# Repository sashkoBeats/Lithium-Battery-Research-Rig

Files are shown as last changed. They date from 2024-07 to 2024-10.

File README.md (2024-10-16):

# Lithium Battery Research Rig
University project development of a rig for 18650 lithium battery testing and research.   
End goal is an EV simulation rig for researching EV battery health and performance.   
Created by Aleksandar Zdravkov and Indra Erkens   
Fontys University of Applied Sciences   
S7 Project and CSA1/2 2022-2024   
   
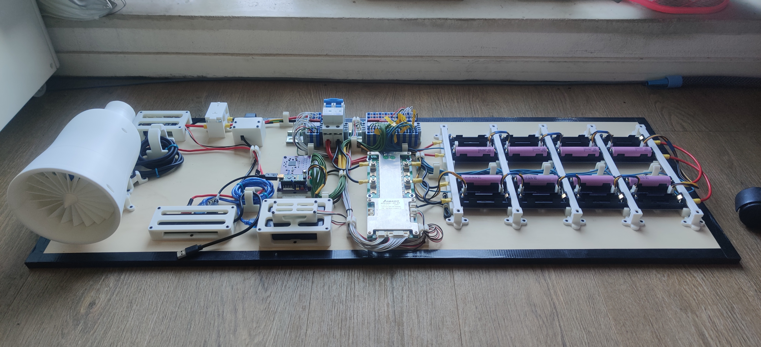
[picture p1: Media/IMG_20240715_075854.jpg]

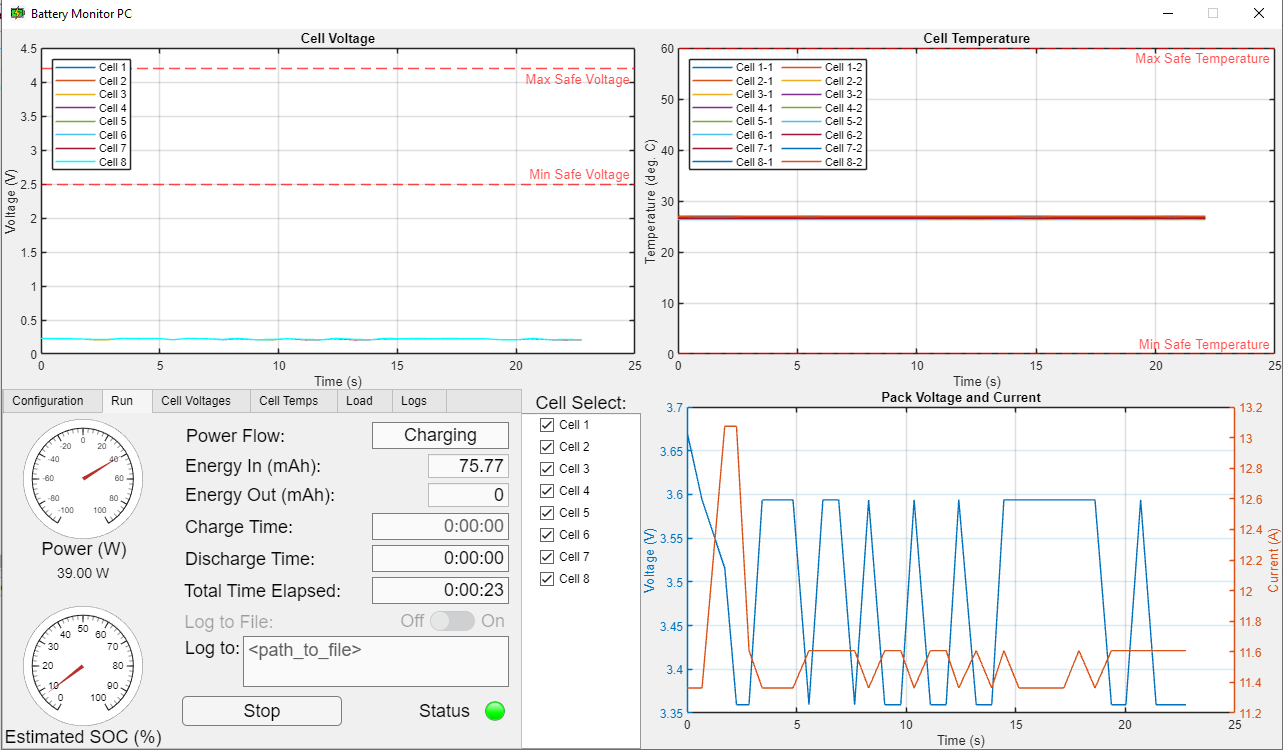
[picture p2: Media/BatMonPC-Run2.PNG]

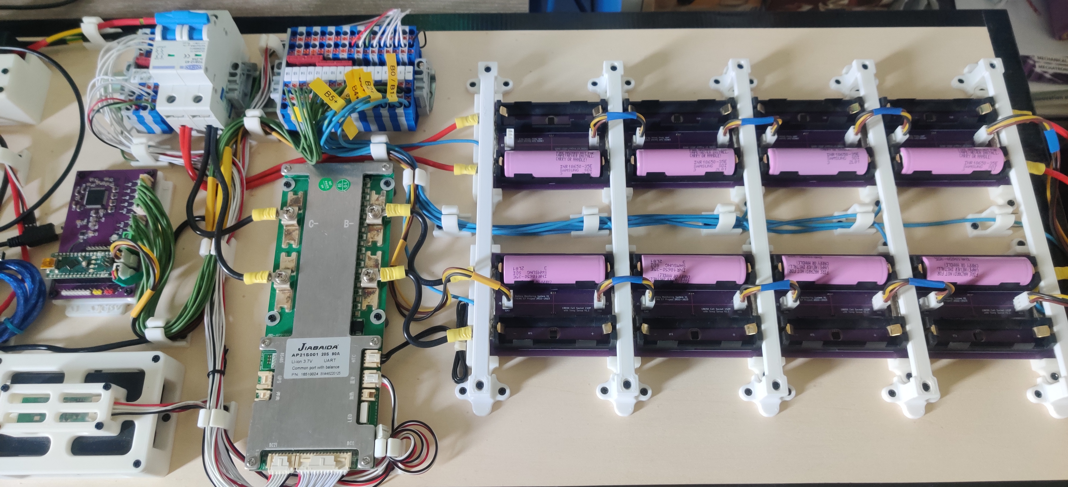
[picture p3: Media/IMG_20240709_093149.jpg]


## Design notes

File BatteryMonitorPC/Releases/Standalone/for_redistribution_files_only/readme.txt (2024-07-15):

BatteryMonitorPC Executable

1. Prerequisites for Deployment 

Verify that MATLAB Runtime(R2022b) is installed.
If not, you can run the MATLAB Runtime installer.
To find its location, enter
  
    >>mcrinstaller
      
at the MATLAB prompt.
NOTE: You will need administrator rights to run the MATLAB Runtime installer. 

Alternatively, download and install the Windows version of the MATLAB Runtime for R2022b 
from the following link on the MathWorks website:

    https://www.mathworks.com/products/compiler/mcr/index.html
   
For more information about the MATLAB Runtime and the MATLAB Runtime installer, see 
"Distribute Applications" in the MATLAB Compiler documentation  
in the MathWorks Documentation Center.

2. Files to Deploy and Package

Files to Package for Standalone 
================================
-BatteryMonitorPC.exe
-MCRInstaller.exe 
    Note: if end users are unable to download the MATLAB Runtime using the
    instructions in the previous section, include it when building your 
    component by clicking the "Runtime included in package" link in the
    Deployment Tool.
-This readme file 

3. Definitions

For information on deployment terminology, go to
https://www.mathworks.com/help and select MATLAB Compiler >
Getting Started > About Application Deployment >
Deployment Product Terms in the MathWorks Documentation
Center.

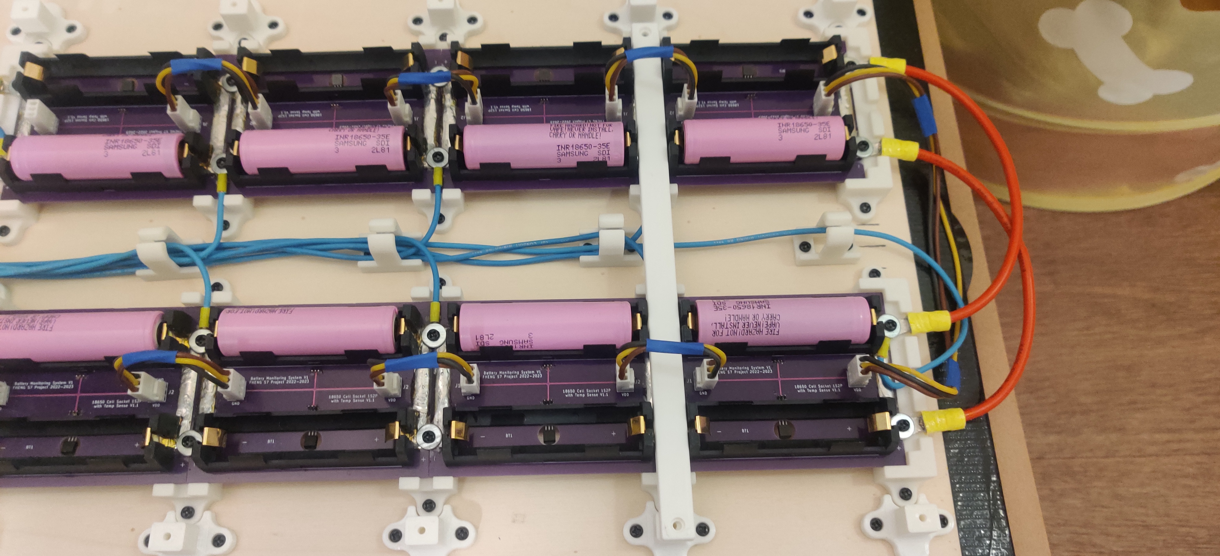
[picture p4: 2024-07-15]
Media/WIP/NiceToHaveFirstAttempt.jpg

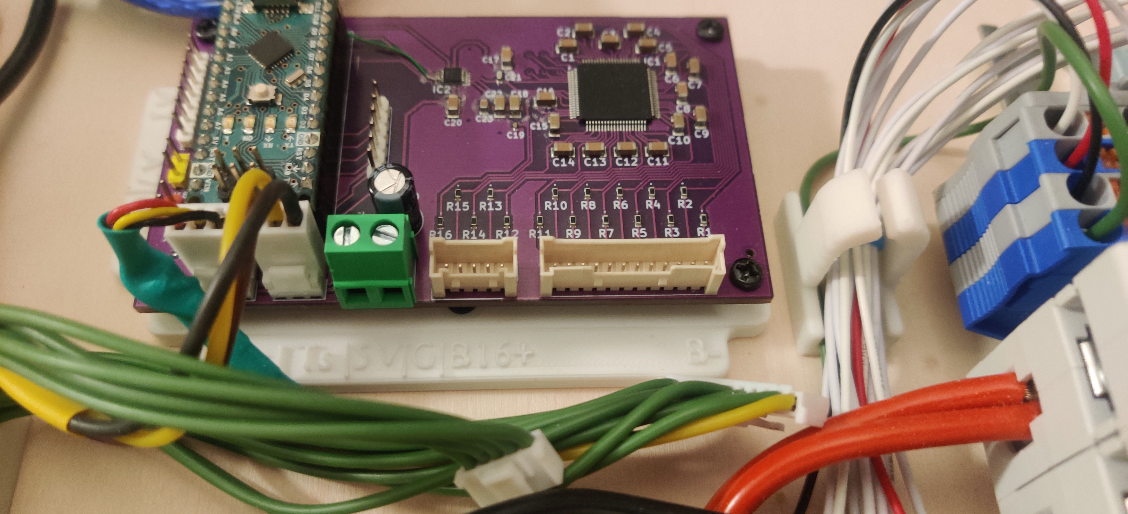
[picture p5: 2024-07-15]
Media/WIP/MonitorboardMount.jpg

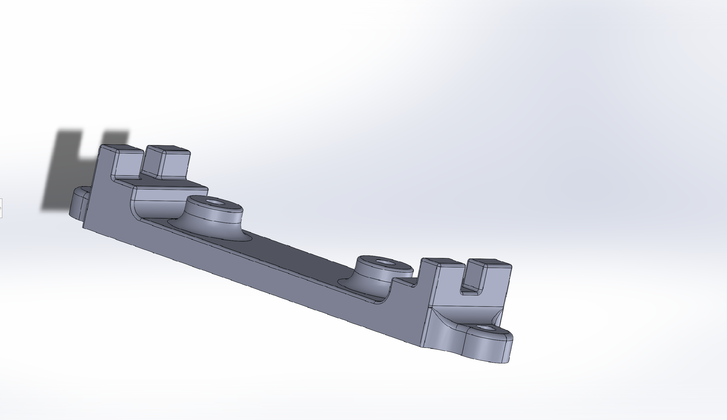
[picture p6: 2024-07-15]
Media/WIP/BatMountV2.png

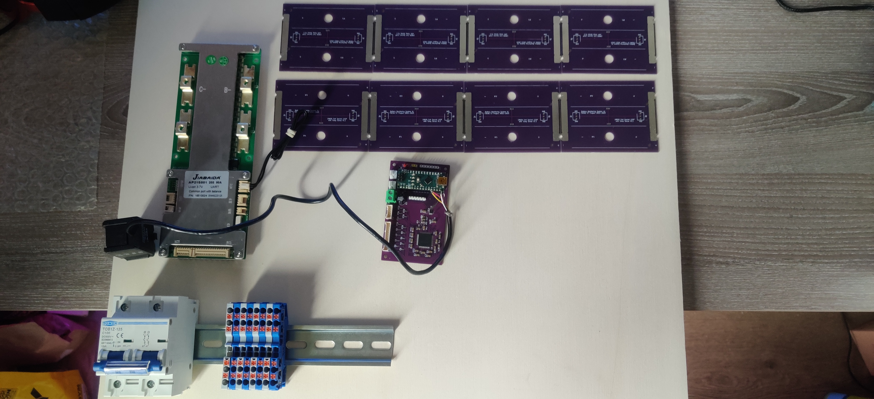
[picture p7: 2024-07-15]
Media/WIP/Layout.jpg

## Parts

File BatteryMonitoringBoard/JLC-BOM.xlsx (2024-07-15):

Comment | Designator | Footprint | JLCPCB Part #（optional）
100uF | C0 | CAPPRD250W50D680H1250 | C109392
1uF | C1, C2, C3, C4, C5, C6, C7, C8, C9, C10, C11, C12, C13, C14, C15, C16, C17, C18, C20, C22 | CAPC3216X180N | C13832
0.1uF | C19 | CAPC1005X55N | C1525
4.7nF | C21 | CAPC1608X90N | C85980
10uF | C23 | CAPC2012X140N | C1713
D_Schottky | D1, D2 | SOD2512X115N | C435857
MAX14921ECS+ | IC1 | QFP50P1400X1400X120-80N | C2932577
3k | R1, R2, R3, R4, R5, R6, R7, R8, R9, R10, R11, R12, R13, R14, R15, R16 | ERJ3EK__0603_ | C278616

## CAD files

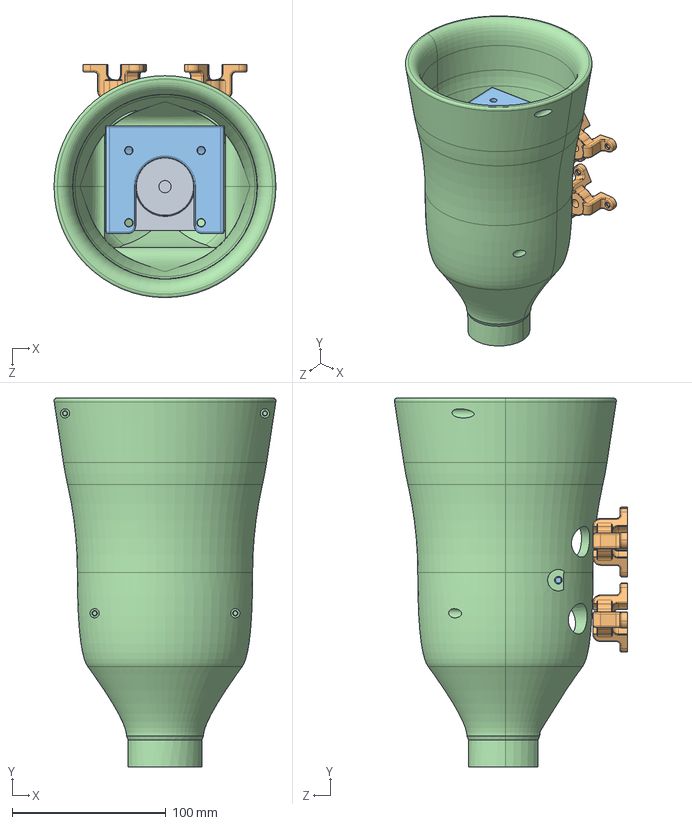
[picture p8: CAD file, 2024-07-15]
CAD/BLDC-Mount-Assy0/BLDC-Mount-Assy.SLDASM
144.3 x 240.0 x 151.7 mm
BatMt-BLDC x 4
BatMt-BLDC-TopV2
BLDC
FanDuct

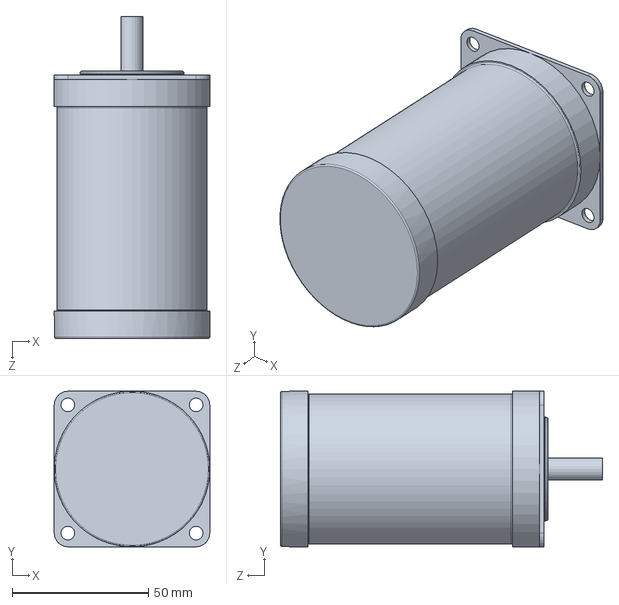
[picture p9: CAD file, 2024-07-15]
CAD/Assembly parts/BLDC.SLDPRT
57.0 x 57.0 x 118.0 mm

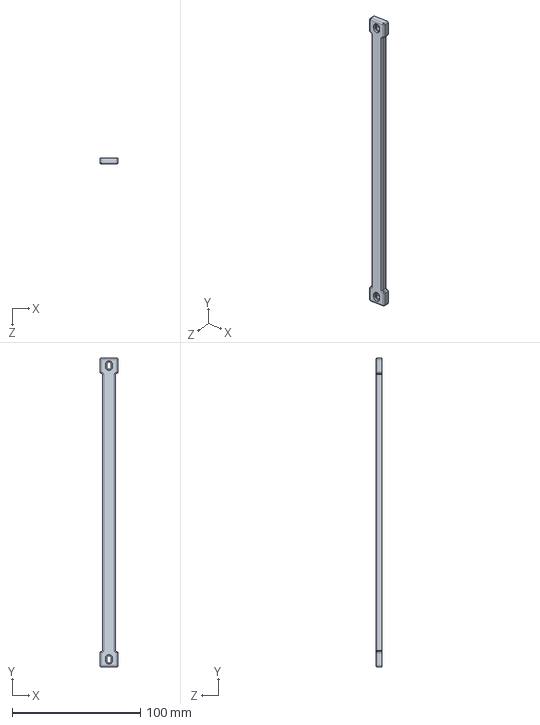
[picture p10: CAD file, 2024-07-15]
CAD/Battery Junction covers/BatMt-CoverV3-Top.SLDPRT
14.0 x 241.0 x 5.00 mm

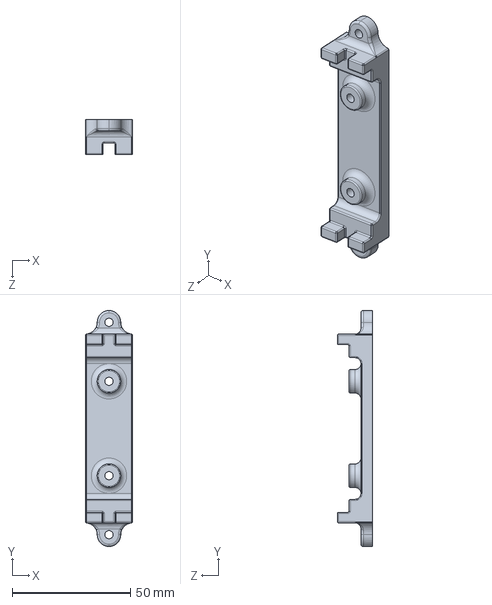
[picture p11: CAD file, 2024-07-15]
CAD/Battery PCB mounts/BatMt-Standoff-V2.SLDPRT
20.0 x 100.0 x 15.0 mm

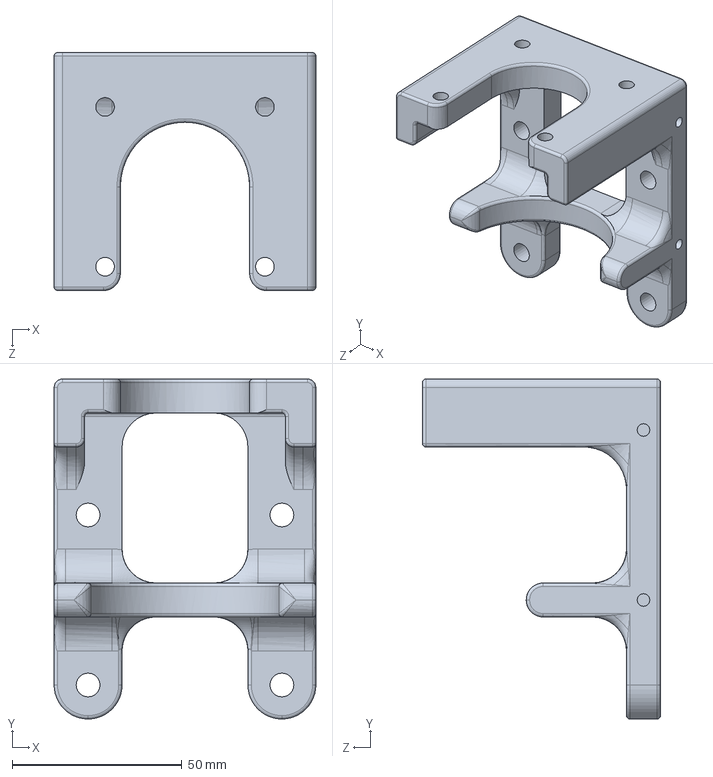
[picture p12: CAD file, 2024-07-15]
CAD/BLDC Bracket/BatMt-BLDC-TopV3.SLDPRT
77.0 x 100.0 x 70.0 mm

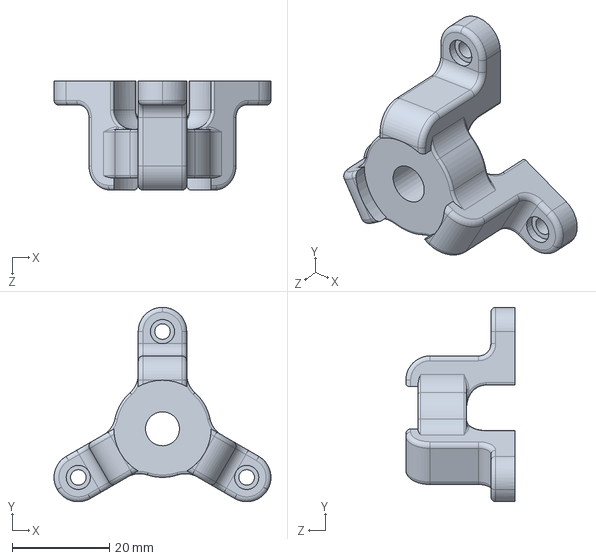
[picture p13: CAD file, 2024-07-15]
CAD/BLDC Mount/BatMt-BLDC.SLDPRT
44.6 x 40.0 x 22.5 mm

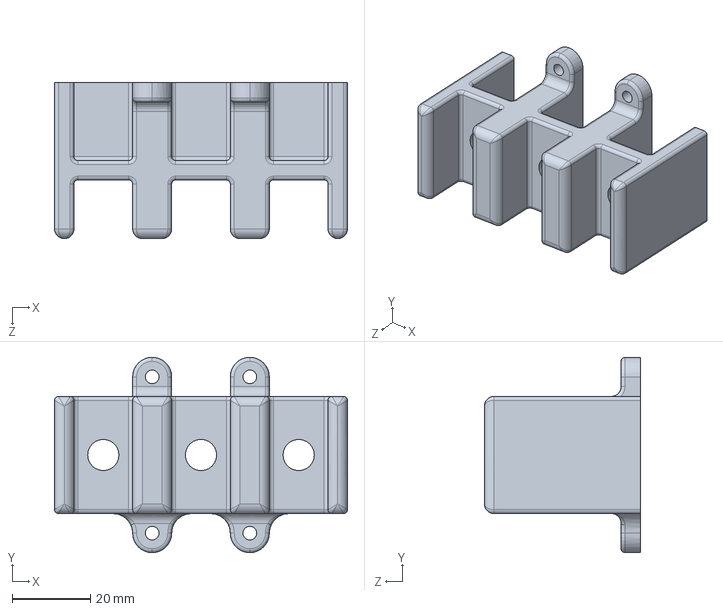
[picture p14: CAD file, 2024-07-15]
CAD/BLDC Power mount/BatMt-BLDC-Plugs.SLDPRT
75.0 x 50.0 x 40.0 mm

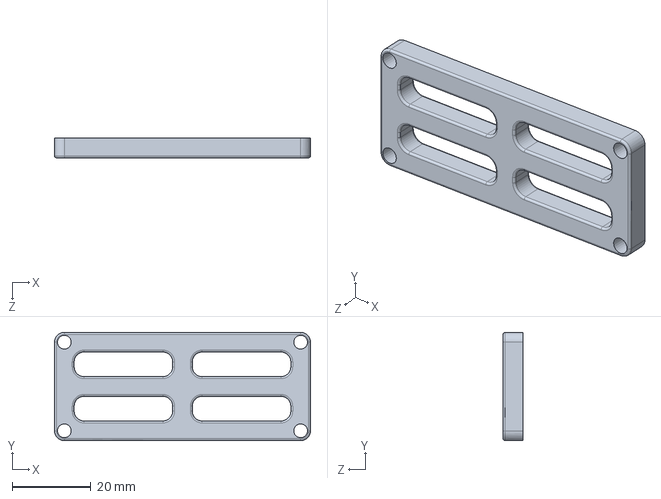
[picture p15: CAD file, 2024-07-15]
CAD/BMS UART box/BatUARTboxTopTop.SLDPRT
65.0 x 27.5 x 5.00 mm

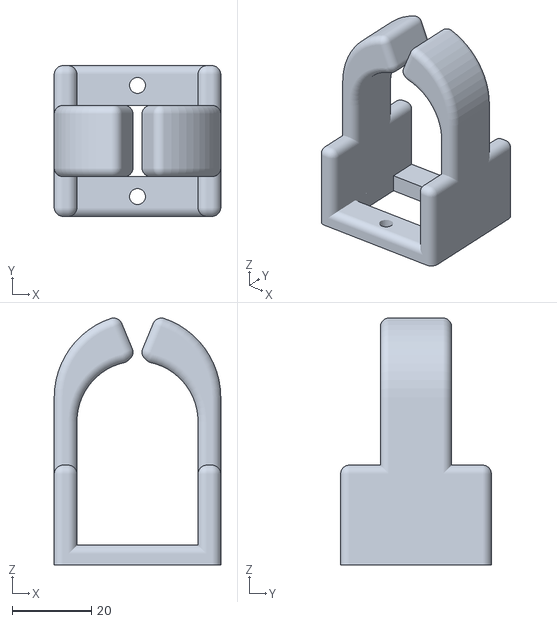
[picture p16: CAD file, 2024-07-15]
CAD/Cable clips/cableclip-large.stl
42.0 x 38.0 x 62.2

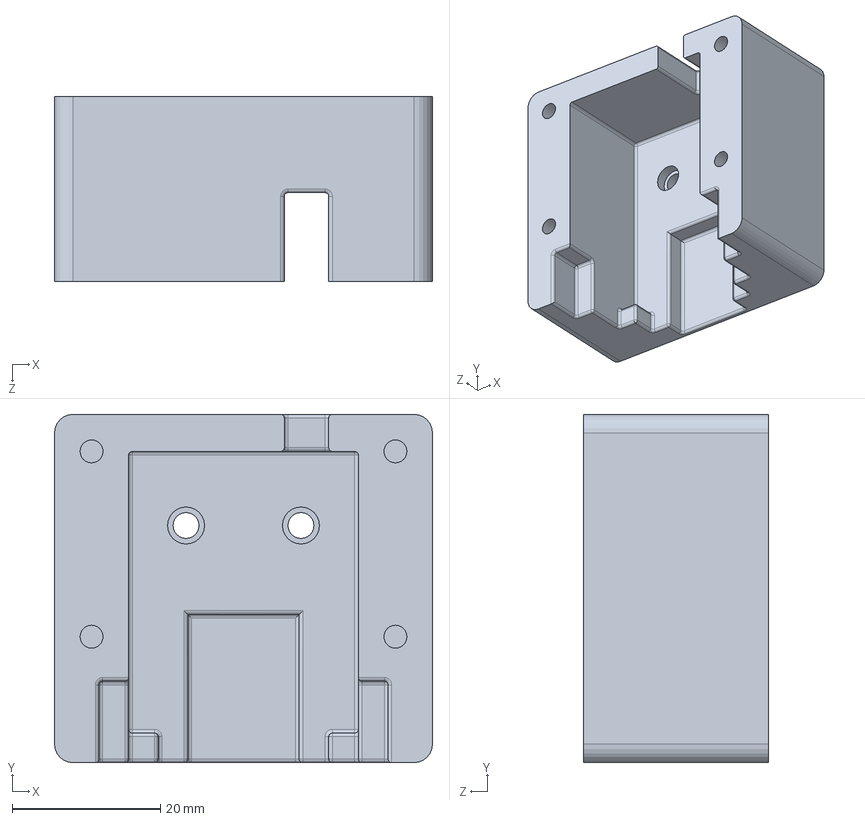
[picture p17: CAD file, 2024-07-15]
CAD/Current Sensor mount/BatMtCC.SLDPRT
51.0 x 47.0 x 25.0 mm

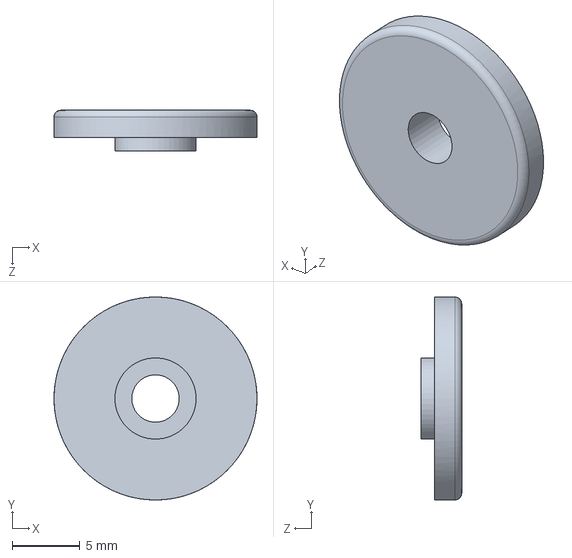
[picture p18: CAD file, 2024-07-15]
CAD/DIN-mount.SLDPRT
15.0 x 15.0 x 3.00 mm

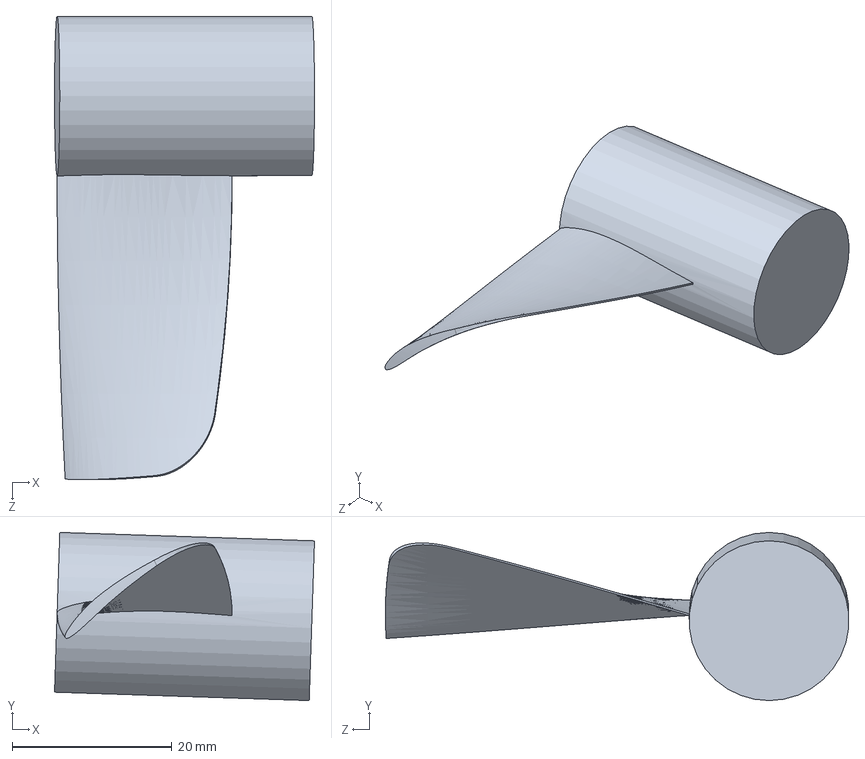
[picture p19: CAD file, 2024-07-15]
CAD/Fan/TurbofanAirfoil.SLDPRT
32.5 x 21.0 x 58.0 mm

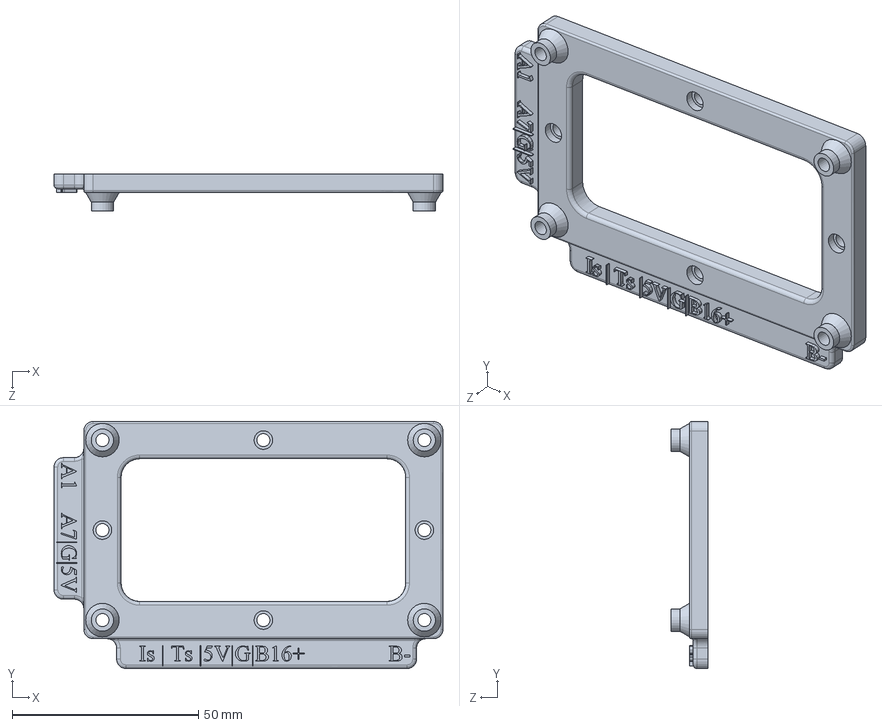
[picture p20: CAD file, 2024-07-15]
CAD/Monitor PCB mount/BatMtMonV2.SLDPRT
104.4 x 66.3 x 10.0 mm

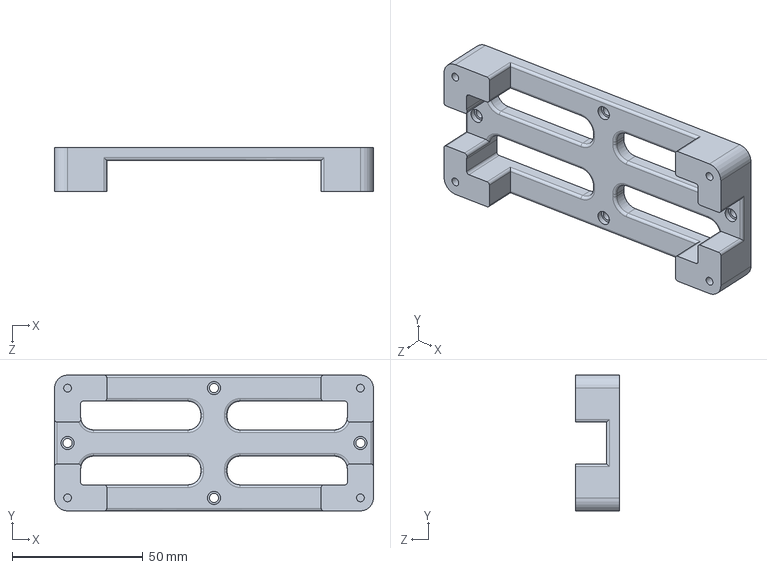
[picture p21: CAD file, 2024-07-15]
CAD/USB Hub box/BatUSBbox.SLDPRT
122.0 x 52.0 x 17.0 mm

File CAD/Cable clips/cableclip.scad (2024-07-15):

/*  cable management clip
    2017-10-13 Russell Salerno
    
    v2 with more automated parameter generation
    notes: open base is preferable as it makes the clamp more flexible & crack-resistant
    
*/


//Clip parameters

// [Distance clip extends from the wall]
depth = 65.5;

// [Height of arms]
height = 18.0;

// [Width of clip, cannot exceed depth]
width = 42.0;

// [Jaw thickness at top]
jaws = 9.0;

// [Space between jaws]
throat = 2.25;

// [Arm thickness]
side_thickness = 3.5;

// [Base thickness]
base_thickness = 5.0;

// [Distance each side wing extends from the arms]
base_sides = 10;

// [Leave at 0 for default ratio of 0.35*height]
base_height_ratio = 0;

// [Minkowski radius for edges]
radius = 2.25;

//Open or closed base? (choose closed if num_holes=1 or 3)
base_type = "open";  // [open, closed]

//Number of screw holes
num_holes = 2;      // [0, 1, 2, 3]

//Hole diameter
hole_diameter = 4;  // [0:10]

//Test render
test_render = true; // [true, false]

module null() {}

//sample sizes
//small
/*
depth = 28;
height = 10.0;
width = 15.0;
jaws = 4.0;
throat = 1.0;
side_thickness = 1.75;
base_thickness = 3.0;
base_sides = 8;
base_height_ratio = 0.25;        // [leave 0 for default]
radius = 0.75;
*/

//small/tall 
/* 
depth = 34;
height = 10.0;
width = 15.0;
jaws = 4.0;
throat = 1.0;
side_thickness = 2.0;
base_thickness = 3.0;
base_sides = 8;
base_height_ratio = 0;        // [leave 0 for default]
radius = 0.75;
*/

//medium
/*
depth = 38;
height = 12.0;
width = 25.0;
jaws = 5.0;
throat = 2.0;
side_thickness = 2.25;
base_thickness = 3.5;
base_sides = 9;
base_height_ratio = 0;        // [leave 0 for default]
radius = 0.95;
*/

//large (original size)
/*
depth = 65.5;
height = 18.0;
width = 42.0;
jaws = 9.0;
throat = 2.25;
side_thickness = 3.5;
base_thickness = 5.0;
base_sides = 10;
base_height_ratio = 0;        // [leave 0 for default]
radius = 2.25;
*/

$fn=60;
minkr=test_render ? 0:radius;   //minkowski takes a while to render, set to zero for testing

clipy=depth-minkr*2;
//clipx=width-minkr*2;
clipx=(width > depth)? clipy:width-minkr*2;     // width can't exceed depth
clipz=height-minkr*2;
clipthk=side_thickness-minkr;
clipjaws=jaws-minkr;
clipbase=base_thickness-minkr;

//throata1=22;
//throata2=25;
throata1=12*(depth/width);
throata2=10*(depth/(width-2*clipthk));
throaty=9/11*jaws;
throatx=throat+2*minkr;

basez=base_sides;
basey=(base_height_ratio == 0)? depth*0.35:depth*base_height_ratio;
baseholed=hole_diameter;

module throat() {
    translate([clipx/2, clipy-clipx/2, 0]) polygon([
        [clipx/2*-sin(throata1), clipx/2*cos(throata1)],
        [clipx/2, clipy],
        [clipx/2*sin(throata1), clipx/2*cos(throata1)], 
        [throatx/2, -throaty+clipx/2],
        [(clipx-clipthk*2)/2*sin(throata2), clipx/2*cos(throata2)-clipjaws-clipthk],
        [(clipx-clipthk*2)/2*-sin(throata2), clipx/2*cos(throata2)-clipjaws-clipthk],
        [-throatx/2, -throaty+clipx/2]]);
}

module base() {
    translate([0, 0, -basez]) linear_extrude(clipz+2*basez) difference() {
        square([clipx, basey]);
        translate([clipthk, clipbase, 0]) square([clipx-clipthk*2, basey-clipbase]);
    }
}

module holes() {
    translate([-minkr, 0, -minkr]) {

        if (num_holes == 1 || num_holes == 3) {
            translate([clipx/2+minkr, base_thickness, height/2]) rotate([90,0,0]) cylinder(d=baseholed, h=base_thickness+minkr);        // hole 1 of 1 hole base
         }

        if (num_holes == 2 || num_holes == 3){
            translate([clipx/2+minkr, base_thickness, -basez/2]) rotate([90,0,0]) cylinder(d=baseholed, h=base_thickness+minkr);        // hole 1 of 2 hole base
            translate([clipx/2+minkr, base_thickness, height+basez/2]) rotate([90,0,0]) cylinder(d=baseholed, h=base_thickness+minkr);  // hole 2 of 2 hole base
        }

        if (base_type == "open") {
            translate([side_thickness+minkr, 0, 0]) linear_extrude(height) square([clipx-clipthk*2-minkr*2, base_thickness]);   // hole for open base
        }
        translate([0, -2*minkr, -basez]) linear_extrude(clipz+2*basez+2*minkr) square([clipx+2*minkr, 2*minkr]);            // flatten the bottom
    }
}

module mainshape() {
    linear_extrude(clipz) difference() {
        hull() {
            square([clipx, 1]);
            translate([clipx/2, clipy-clipx/2, 0]) circle(d=clipx);
        }
        hull() {
            translate([clipthk, clipbase, 0]) square([clipx-clipthk*2, 1]);
            translate([clipx/2, clipy-clipjaws-(clipx-clipthk)/2, 0]) circle(d=clipx-clipthk*2);
        }
        throat();
    }
    base();
}


rotate ([90, 0, 0]) difference() {
    minkowski() {
        mainshape();
        sphere(r=minkr);
    }
    holes();
}

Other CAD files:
CAD/BLDC-Mount-Assy/BLDC-Mount-Assy.SLDASM
CAD/VESC box/BatVESCbox.SLDPRT
CAD/VESC Power In/BatVESCPowerBlockTop.SLDPRT
CAD/Assembly parts/Rubber-mount.SLDPRT
CAD/BLDC Bracket/BatMt-BLDC-Top.SLDPRT
CAD/BLDC Bracket/BatMt-BLDC-TopV2.SLDPRT
CAD/BLDC Mount/BatMt-BLDC.STL
CAD/BLDC Power mount/BatMt-BLDC-Plugs.STL
CAD/BLDC-Mount-Assy/FanDuct.SLDPRT
CAD/BLDC-Mount-Assy/FanDuctBot.SLDPRT
CAD/BLDC-Mount-Assy/FanDuctBot.STL
CAD/BLDC-Mount-Assy/FanDuctTop.SLDPRT
CAD/BLDC-Mount-Assy/Rubber-mount.SLDPRT
CAD/BLDC-Mount-Assy/TurboFan.SLDPRT
CAD/BLDC-Mount-Assy0/FanDuct.SLDPRT
CAD/BLDC-Mount-Assy0/Rubber-mount.SLDPRT
CAD/BLDC-Mount-Assy0/TurboFan.SLDPRT
CAD/BMS UART box/BatUARTbox.SLDPRT
CAD/BMS UART box/BatUARTbox.STL
CAD/BMS UART box/BatUARTboxTop.SLDPRT
CAD/BMS UART box/BatUARTboxTop.STL
CAD/BMS UART box/BatUARTboxTopTop.STL
CAD/BatMt-General-standoff-V2.SLDPRT
CAD/BatMt-General-standoff-V2.STL
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

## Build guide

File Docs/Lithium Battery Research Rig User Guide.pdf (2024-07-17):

# Lithium Battery Research Rig

# User Guide

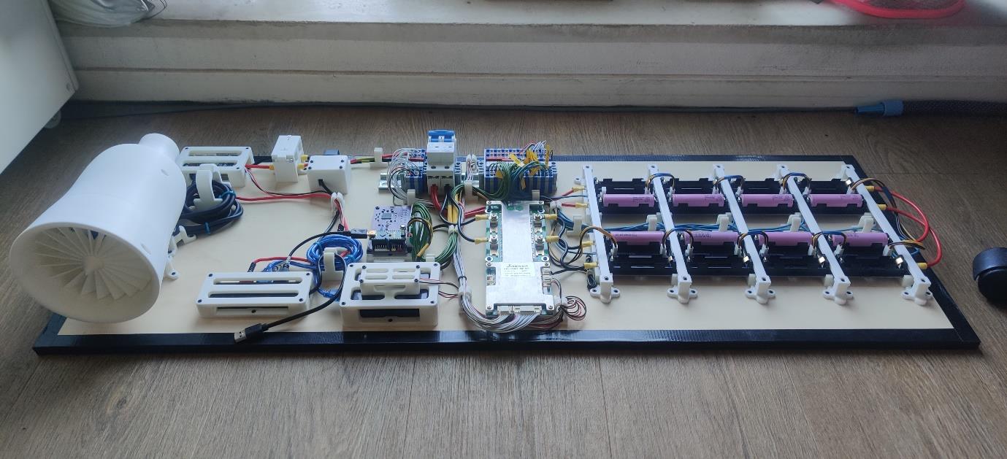
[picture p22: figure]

## Aleksandar Zdravkov Eindhoven

16/07/2024

## Table of Contents

Definitions | 3
SAFETY INFORMATION | 4
IMPORTANT INFORMATION | 5
Introduction | 5
Preparation for use | 7
Battery Monitor PC Application | 10
Preparation for storage | 12
Storage | 13
BMS | 13
Temperature sensors | 18
Load | 19
Resources | 19

Figure 1: Battery cell section of rig. Line of red dashes shows where to cut cables and break
board in case of terminal battery fault | 4
Figure 2: Battery Research Rig Setup | 5
Figure 3: Cold and dark battery rig | 7
Figure 4: First cell insert | 8
Figure 5: All cell holders populated for 8s1p configuration | 8
Figure 6: JDB BMS Homescreen after power up. All 8 cells detected | 9
Figure 7: Battery Monitor PC Configuration tab | 10
Figure 8: Battery Monitor Run tab | 11
Figure 9: Battery Monitor Run tab while running | 12
Figure 10: JBD Smart BMS mobile app dashboard | 14
Figure 11: JBD Mobile app navigation pane | 15
Figure 12: JBD Mobile app parameter settings page | 16
Figure 13: JBD Mobile app function setting page | 17
Figure 14: 18650 Lithium cell holder PCB with built-in DS18B20 digital temperature sensors... 18 Figure 15: Arduino program for detecing the unique device IDs of DS18B20 temperature
sensors | 19

# Definitions

AC | Alternating Current
ADC | Analog to Digital Converter
BMS | Battery Management System
BLDC | Brushless DC (Motor)
CAD | Computer Aided Design
CSA | Curriculum Supporting Activity
DC | Direct Current
DIY | Do-It-Yourself
EV | Electric Vehicle
ESC | Electronic Speed Controller
FET | Field Effect Transistor
GND | Ground
LFP | Lithium Iron Phosphate (LiFePO4)
R&D | Research and Development
RPM | Revolutions Per Minute
SOC | State of Charge
UART | Universal Asynchronous Receiver-Transmitter
USB | Universal Serial Bus

# SAFETY INFORMATION

This battery test and research rig is intended for use with 18650 size Lithium-based batteries. Most common of these are Li-Ion and Li-Poly, commonly found in smart devices (phones/laptops/tablets/etc.) and EV battery packs. These chemistries are incredibly dangerous as mishandling of the battery or subjecting it to abnormal operating conditions could cause it to enter a thermal runaway state. This is a terminal fault as Li-Ion and Li-Poly cells produce pure oxygen as a byproduct of the lithium in the cell reacting with the air and the other compounds in the cell structure as it’s disintegrating on fire. Therefore, a Li-Ion/Poly cell fire CANNOT be extinguished as the fire is essentially producing its own fuel. This generally does not apply to LiFePO4 batteries as their chemical composition makes them much more stable. When in thermal runaway state, LFP cells do not produce their own oxygen fuel. Instead, a failing LFP cell simply vents its electrolyte compound (PO4) as a gas/vapor through a one-way relief valve. The temperature reached during thermal runaway of LFP cells is also typically not high enough to cause an uncontrolled fire.
For the safety of the students and Fontys Engineering, it is important that students given access to this rig are well informed about the operational principles and hazards of lithium-based batteries. When the rig is in use, it MUST ALWAYS be accompanied by a container full of sand and/or dirt that can be used to dump a failing cell into to burn up in safety (as mentioned above, once a cell is in thermal runaway, it cannot be saved). If a cell fails (starts smoking/swelling/burning) while installed on the rig, pour the sand/dirt on top of it to try to limit the spread to the other cells in the rig. If the failing cell was successfully contained, wait for it to cool off and carefully remove it from the rig. The cell-holder PCB can be easily replaced if it suffers damage. In case covering a failing cell with sand/dirt does not contain the fire, you can attempt to save the rest of the setup by cutting all the wires between the batteries section of the rig and the electronics. This will allow you to break-off the batteries section of the plywood board and let it burn, saving the expensive monitoring electronics, BMS, loads, etc. ONLY DO THIS IF YOU ARE CONFIDENT YOU HAVE ENOUGH TIME UNTIL FIRE IS COMPLETELY OUT OF CONTROL TO EXECUTE THE PROCEDURE. IF UNSURE, JUST RUN AWAY AND CALL FOR HELP.

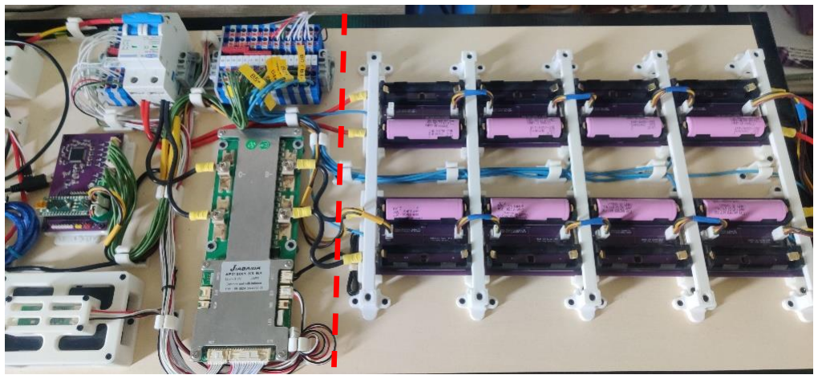
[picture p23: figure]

Figure 1: Battery cell section of rig. Line of red dashes shows where to cut cables and break board in case of terminal battery fault.

# IMPORTANT INFORMATION

Never leave battery cells in the rig unattended, especially while in storage! The BMS and Battery Monitoring board will draw power from any cells left in the holders and gradually drain them to 0V. Dropping below minimum spec sheet voltage is very bad for lithium cells so it should never be allowed to happen. Removing just the first or last cell in the stack does NOT prevent the drain from occurring in the other cells! ALL CELL HOLDERS MUST BE EMPTY WHEN THE RIG IS NOT IN USE!
It should go without saying that nothing “dumb” shall be done with any lithium cells at any point, especially when a cell is under load (DUT), that risks the safety of people and/or the research rig. Hitting, puncturing, burning/heating/freezing, overloading, shorting, or otherwise subjecting lithium cells to abnormal conditions can be deadly to you and your colleagues. Exercise great care and be on high alert when working with this rig and with lithium batteries in general!

# Introduction

This user guide goes over all the information related to the use of the lithium battery research rig. The rig was created over a span of 2 academic years, starting as a semester 7 project in the 2022-2023 academic year. The S7 project ended with only a general schematic of the intended final product and the PCB design of the battery monitoring board. As part of CSA 1 and 2 over the following 1.5 years, the project was worked on by 2 students in their free time in-between internships and work. The rig gradually took shape with additional functionality added to make it more feature complete. As of writing this guide, the rig is only missing a controllable mechanical load in order to be a fully functional EV simulation device. The rig is intended to be used by Fontys students to study health and performance of lithium batteries and by extension, EV battery packs. There are many topics of interest for research and development, but they will be discussed in a separate guide. The GitHub repository hosting this project includes all source code, CAD files, schematics, data sheets, etc. that were used in the execution of the project.

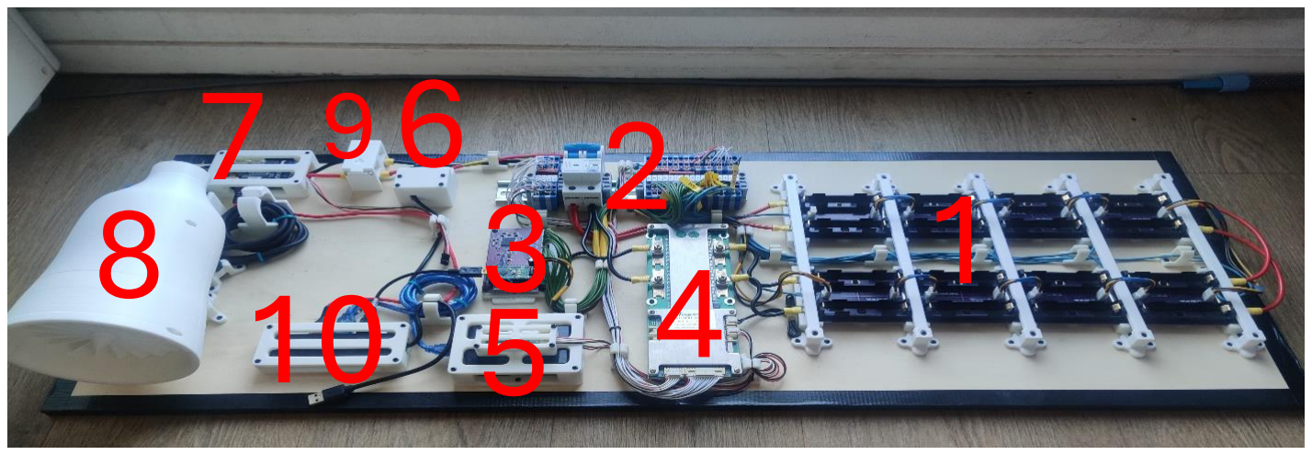
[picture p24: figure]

Figure 2: Battery Research Rig Setup.
Based on the figure above, a short description of each main component of the rig can be found below:

### 1. Battery cell stack

The rig is designed around an 8 series cells with 2 parallel for each (8s2p) configuration of 18650 Li-Ion/Poly/FePO4 batteries. This configuration and slight variations of it (+-1/2 cells in series or parallel) are commonly used for smaller personal EVs like E-bikes, E-scooters, E-skateboards, etc. The cells are laid out in quick-swappable cell holders on custom PCBs in 2 sections of 4 series PCBs. Pay attention to the direction of the sections – they are mirrored symmetrically, meaning the positive and negative side invert between the sections. Pay close attention to the polarity of the cells when installing them in the holders. Each battery holder PCB also has a digital temperature sensor installed underneath each cell. These are connected to the battery monitoring board via their dedicated 3-wire cables in daisy-chain configuration.

### 2. Distribution “box”

All cell taps (wires to each individual cell) are wired to a dedicated (for each cell) DIN-rail 4-port wire socket. The battery monitoring board and BMS connect to the box with the appropriate wiring scheme for correct operation of each device. Each wire socket has 1 port left uncopied, for future use (see R&D Guide). The box also includes a main DC-rated circuit breaker between the battery stack and any loads.

### 3. Battery Monitoring Board

Customed designed PCB housing a MAX14921 16-cell battery monitoring IC, a MAX11161/11163 16-bit ADC, and a socketed Arduino Nano MCU. The Arduino Nano interfaces with the 2 MAX chips via SPI to get battery and cell voltage data. It also fetches temperature data for each cell from the daisy chain and the current sensor data for total battery pack current. The data is transferred to PC in raw format via Serial for processing in real time with the help of a dedicated MATLAB Application.

### 4. JBD BMS

This is a commercial smart BMS that allows manual tuning of a wide variety of lithium battery protections. The BMS is required to keep the battery from unintentionally entering abnormal conditions. It’s configured for Li-Ion cells currently but needs to be reconfigured when different cell chemistries are used.

### 5. JBD Bluetooth and UART modules

These are the interfaces available for connecting with the JBD BMS. Only one of them can be used at a time since they share the same communication port on the BMS. By default, the BT module is connected, as it’s easier to configure the BMS with the smartphone app. Alternatively, the UART box can be connected instead and used in conjunction with an open-source application, BMS Tools JBD, which allows for monitoring and control of the BMS from a PC.

### 6. Current Transformer (sensor)

A split-core current transformer used to measure the total current going in or out of the battery pack. The sensor is bi-directional and rated for DC measurement. In the rig, the positive wire of the battery pack goes through the sensor. The sensor is rated for 5V power and signaling, providing an analog signal for measurements, which is read by the Arduino Nano.

### 7. Flipsky VESC 4.12

The electronic speed controller used to convert the battery pack’s DC power to 3-phase AC for driving the BLDC motor load. The VESC is extensively customizable, allowing for great load control when developing EV simulation runs.
8. 150W Electric Skateboard BLDC
A relatively big BLDC motor rated for up to 36V and up to 8A current draw to be used as an electrical load for the battery pack. The motor does not consume much power to reach its max RPM when no mechanical load is placed on it, which means it needs a controllable mechanical load to make the rig fully operational. Until such a solution is created or found, a turbine-type engine was built around the motor to keep it cool (it heats up when running for a while with no load).

### 9. Battery DC I/O Port

Underneath the plastic cover are 2 banana plug receptacles coming from the battery positive and negative wires. The port can be used for a variety of things, such as charging the whole battery stack, attaching external loads, or just probing for measurements. 10.USB Hub
Since the BMS, the battery monitoring board and the VESC all have USB interfaces for PC communication, a small USB hub is incorporated to simplify the connection to a PC for use with the rig.

# Preparation for use

This chapter covers the steps to take from “cold and dark” to configure the rig for use. When you begin work, the rig should look like the figure below, with no cells installed and DC circuit breaker in the OFF position.

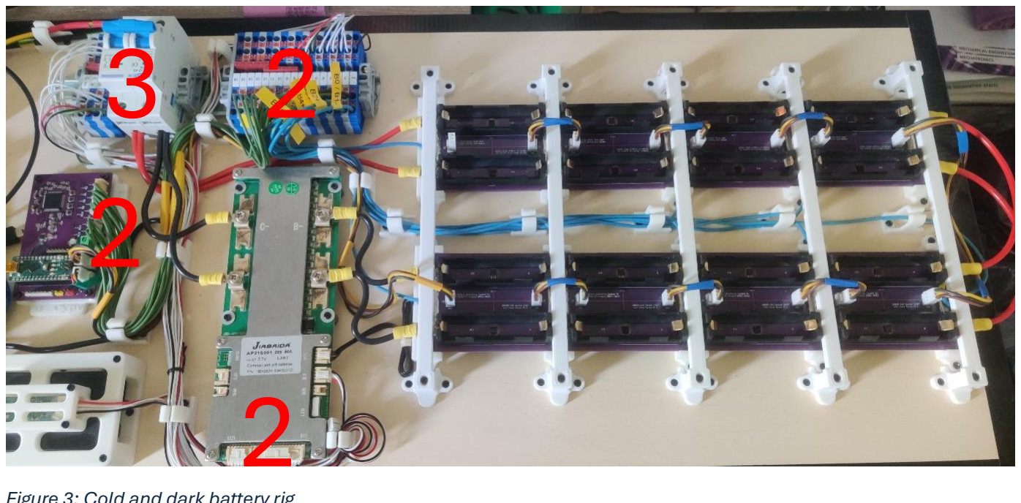
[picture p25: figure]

Figure 3: Cold and dark battery rig.
1. First, inspect the whole rig for any abnormalities, disconnected wires, etc. Once you make sure everything is looking proper, proceed with cable check.
2. Check all cables – All cell taps should be connected to their proper position in the cell stack and the distribution box. Check the BMS and battery monitoring board cables harnesses are connected.
3. With the DC breaker OFF, battery cells may now be inserted into the slots.
4. Insert cell into each holder, starting with cell 0 (closest to negative wires). If only 1 cell per segment in the series stack is used (so, 8s1p configuration), populate either only the BT1 or BT2 slots for each cell holder in the series. Pay attention to cell polarity!

4

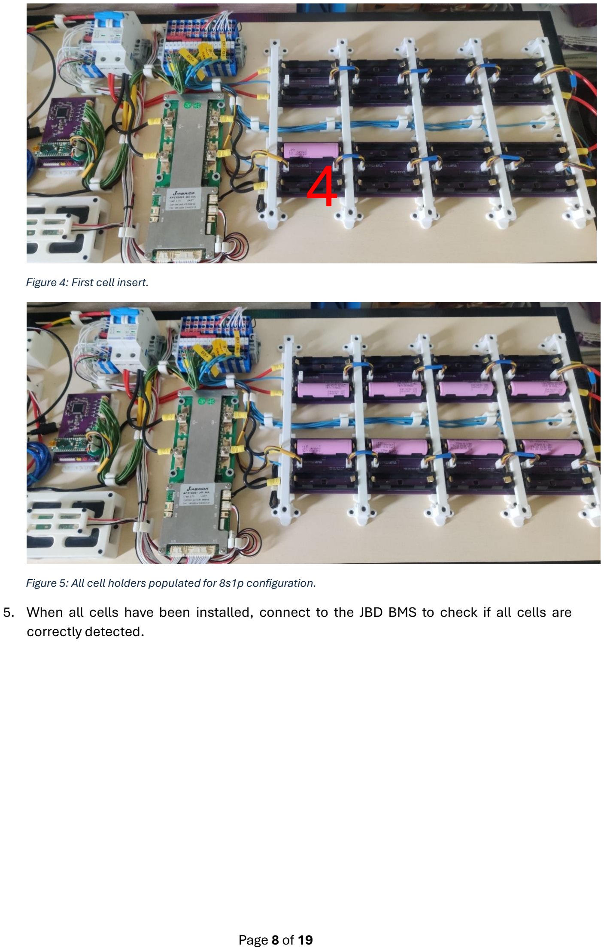
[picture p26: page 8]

Figure 4: First cell insert.

Figure 5: All cell holders populated for 8s1p configuration.
5. When all cells have been installed, connect to the JBD BMS to check if all cells are correctly detected.

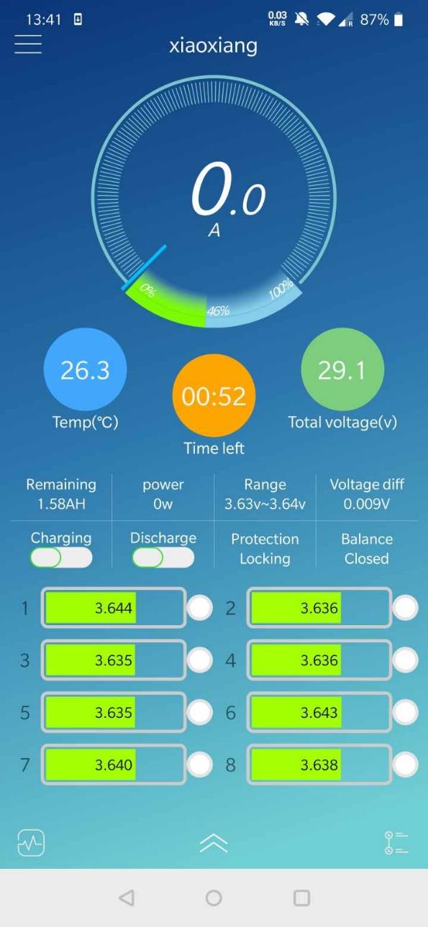
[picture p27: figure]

Figure 6: JDB BMS Homescreen after power up. All 8 cells detected.
6. Once the pack is correctly installed, the USB hub can be connected to a PC to power up the Arduino Nano on the battery monitoring board and provide an interface to the JBD UART box and the VESC.
7. The MATLAB Battery Monitor PC application can now be started and a connection with the Arduino Nano on the monitoring board can be established. The instructions for using the application can be found in the next chapter.
8. With the PC application configured and connected to the battery monitoring board, testing runs can executed.
9. Check that an adequate load is correctly attached to the DC circuit breaker. If all is good, flip the circuit breaker to the ON position. The VESC should light up and appear as a new COM port on the PC connected to the USB hub.
NOTE: If the load/VESC does not power up, check that the JBD BMS has switched on its Discharge FETs.
10. With the load configured and online, the battery rig is ready for science. Students shall prepare a test plan or protocol to conduct and commence its execution at this point.

# Battery Monitor PC Application

In order to process the incoming battery data from the monitoring board, a special MATLAB App was developed. The application polls the battery monitoring board at a user defined polling rate (0.5s default, 0.2s minimum) for all battery data that it collects (voltage, current, temperature) in raw format. The data is converted to usable values and displayed on 3 MATLAB graph windows. The application is packaged both as a MATLAB App module and as standalone application installer that includes a MATLAB runtime necessary to run. So MATLAB is technically not required to run the app. The main functions of the app are described below. Most fields and widgets in the application also show a helpful tooltip when hovered upon with the mouse pointer to guide the user.

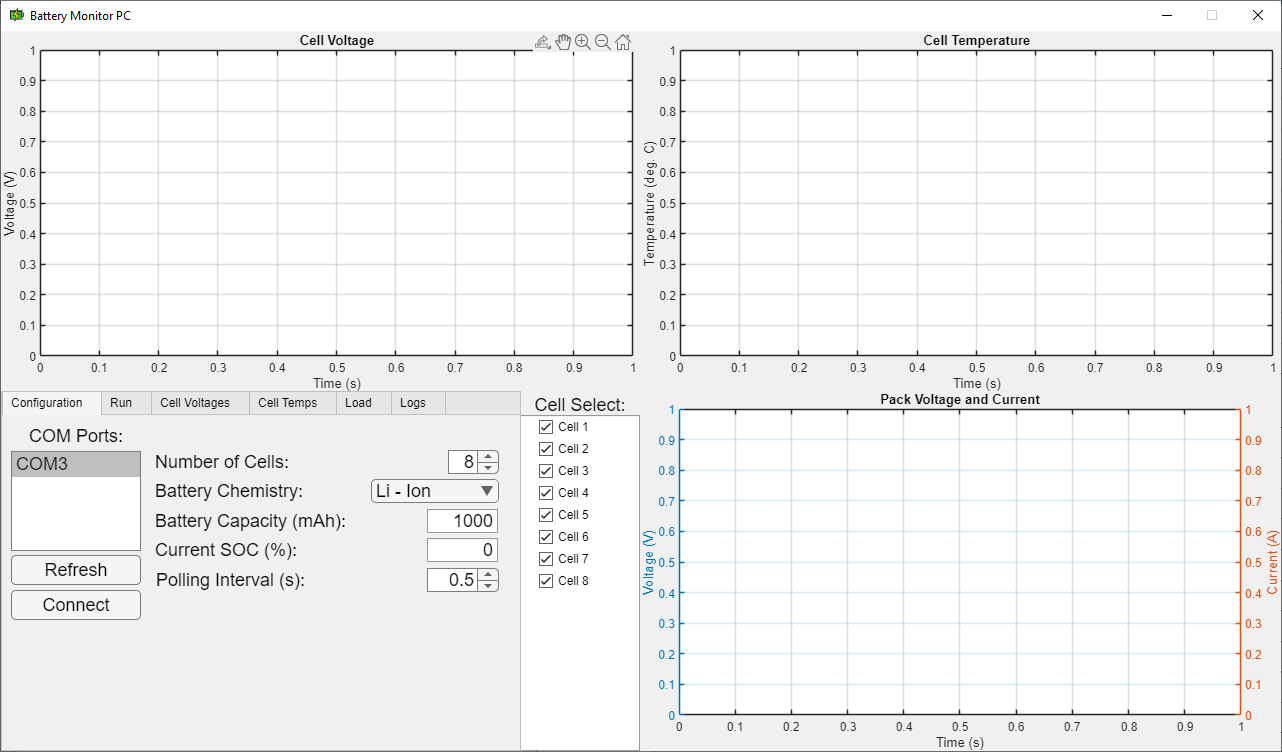
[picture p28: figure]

Figure 7: Battery Monitor PC Configuration tab.
The figure above shows the interface of the Battery Monitor PC application when it’s launched. The top left and the two right quadrants of the application window are permanently occupied by the voltage, temperature and voltage/current graphs. The bottom left quadrant is where all the control UI is located, separated into tabs that group related functionality and/or data displays together. If the battery monitoring board is plugged in, it will show up as a COM port in the list at the left of the Configuration page. To the right of it are the parameters for the cell stack currently installed in the rig. All values except current SOC and rated battery capacity MUST be configured before connecting to the Arduino on the monitoring board, as they are required for configuration of the Arduino and will become locked after hitting “Connect”. Once connected to the monitoring board Arduino, cyclic data polling will start at the specified polling rate, but the graphs will not work at this time. To go easy on the PC running the app, the graphs are only going to start updating once a test run is initiated via the Run tab. If it’s needed to check battery data before starting a run, the fields in the Cell Voltages and Cell Temps tabs will always update any time there is new data available. The Cell Select window scales automatically with the number of cells selected and only controls which cell data is displayed on the graphs. The data for all cells up to the selected number of cells is always retrieved from the Arduino and written to the file log, if enabled. Once configured and connected to the Arduino, the Run tab becomes the main window for the bottom left quadrant of the app.

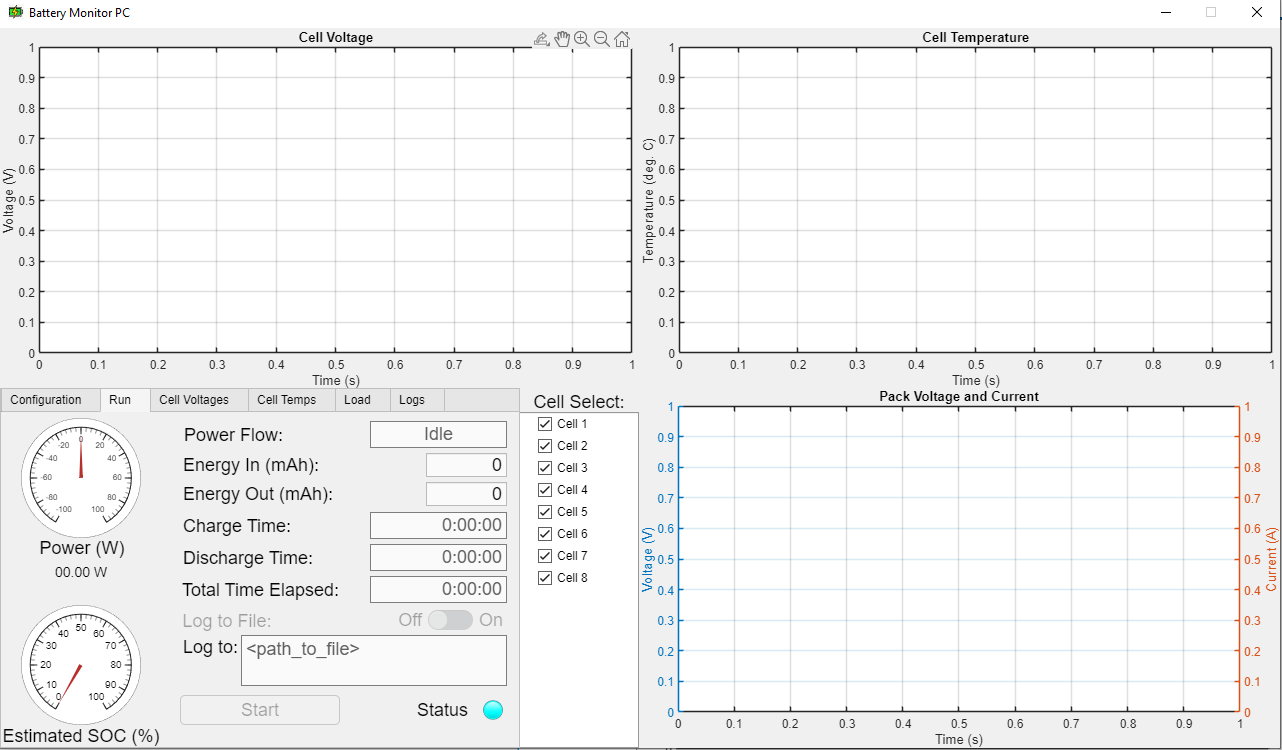
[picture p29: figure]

Figure 8: Battery Monitor Run tab.
The run tab shows the information relevant to the test run being conducted, such as timers, energy meters, a state-of-charge (SOC) estimate and power flow. The tab also contains the interface for configuring file logging. If the Log to File button is flipped to On, a prompt will pop-up to select file name and location for the log file. Once a valid file and location are successfully specified, the application will be configured to record all incoming battery data after the Start button is pressed to the specified file in a csv format. The log file can then be processed with MATLAB scripts to recover test run data. After pressing the Stop button (Start button turns to Stop button when pressed), a test run is concluded and the log file (if enabled) is closed. The Log to File switch is reset back to Off. A new log file must be specified by repeating the procedure for any subsequent test runs. During a test run, the 3 graphs will start updating at a rate close to real-time with the incoming voltage, current and temperature data.


Figure 9: Battery Monitor Run tab while running.
The safe voltage and temperature lines on the top quadrant graphs are determined by the selected battery chemistry in the Configuration tab at the start. There are also a load control tab and logs tab in the control quadrant, but these were not implemented due to time. The visualization is intended to help students quickly observe the diverging behavior of cells in a battery pack that occurs due to a variety of factors such as aging, performance degradation with use over time, manufacturing tolerances, etc. More about the research use of this rig can be found in the R&D guide.
Note: It is recommended that an ongoing run is stopped and the Arduino disconnected from the Configuration tab before closing the application, but the app will try to handle that for the user if they forget.

# Preparation for storage

When a testing session has concluded, the rig must be prepared for storage. The sequence generally follows the setup for use sequence, just in reverse order.

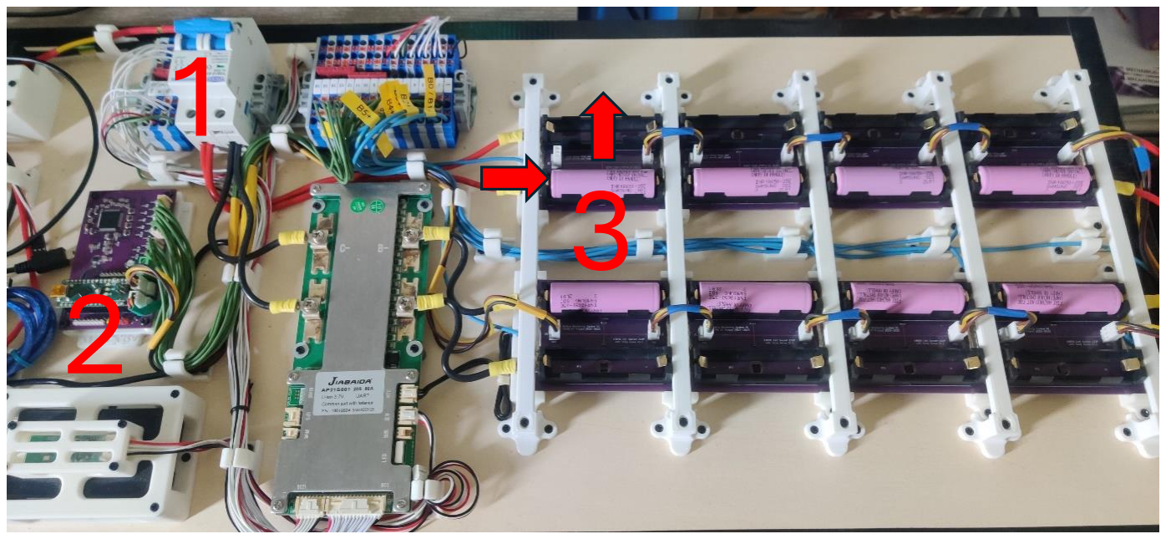
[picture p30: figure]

1. Disconnect all loads by flipping the DC circuit breaker to the Off position.
2. Unplug the USB Hub and/or monitoring board Arduino from PC.
3. Start dismounting battery cells from the start, beginning with the top cell (8) and working back to cell 1. The easiest way to get a cell out of the tight holders is to push it back with a finger from the positive terminal side back towards the negative and grip the cell in the middle with the other hand, pulling/pushing upwards to release the cell.
4. Once all cells are out of the rig, make sure to tie any loose cables and wires and put the rig back in its nylon bags and put it away in safe location. No prolonged exposure to direct sunlight!

# Storage

When the rig is in storage, there must be no cells left in it in any cell holder! The DC circuit breaker must be in the Off position and the rig should be covered to avoid dust accumulation in tight spaces. Since there are a lot of 3D printed parts on the rig, prolonged exposure to direct sunlight, high temperatures or humidity are to be avoided. In general, the rig should be treated with care both when in use and when in storage.
Any battery cells dedicated for use with this rig should be stored separately, at 30% state-of-charge and periodically topped up with a charger back to 30% if the rig is dormant for a while.

# BMS

The rig utilizes a commercially available smart BMS for lithium batteries from Chinese manufacturer JBD. Smart BMS allows for pretty much all protection settings (trigger thresholds, protection trigger delays, protection recovery thresholds, etc.) to be manually configured to an appropriate value for the specific lithium battery chemistry used on the rig. The BMS is included in the rig to protect the battery cell stack and students in case something unplanned happens. However, for some interesting tests that can be performed, it would be desirable to put the battery cell stack in what would normally be considered abnormal condition, causing the BMS to trigger protections. Therefore, a smart BMS is required. The JBD BMS is widely used for personal DIY EVs and EV battery packs, as well as solar energy storage server rack LFP batteries. As a result, there is a free utility available on GitHub for connecting to JBD smart BMS boards from a PC (via the

UART box). The utility can read all measurements and settings from the BMS and even log battery data to csv files. This is very useful in case there are problems with the custom battery monitoring board. However, for most of the time, it would probably be easier to operate the BMS via its mobile app (available from JBD website). Below is a quick guide for it:

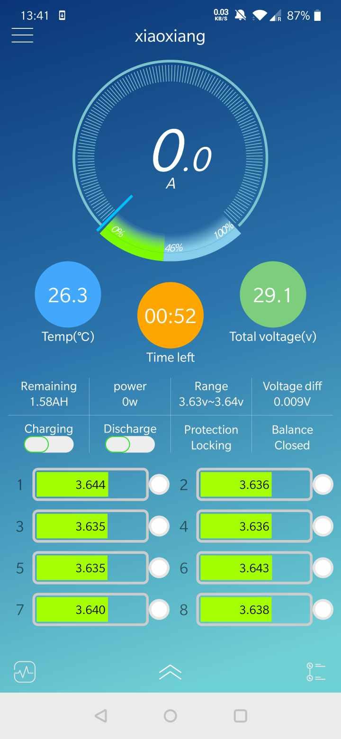
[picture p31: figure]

Figure 10: JBD Smart BMS mobile app dashboard.
On the figure above is the home page of the mobile JBD BMS app (Xiaoxiang). The page shows the most important battery data, such as cell voltages, pack voltage and current, temperature, and charge/discharge control. Pressing on the burger menu in the top left corner opens the app navigation pane:

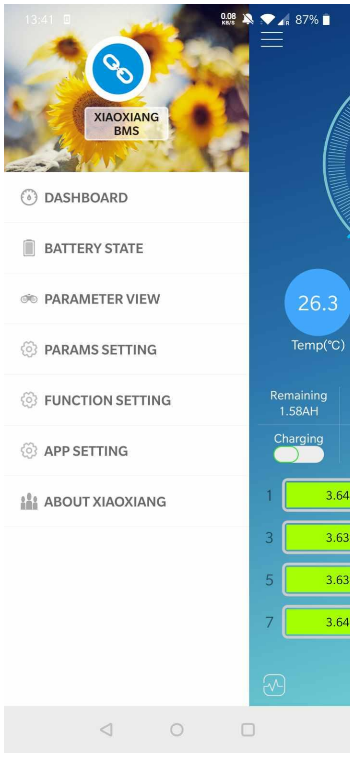
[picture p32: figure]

Figure 11: JBD Mobile app navigation pane.
From here, the most important menus are the parameter view/setting (they lead to the same page) and function setting. The parameter menu is self-explanatory, example figure below.

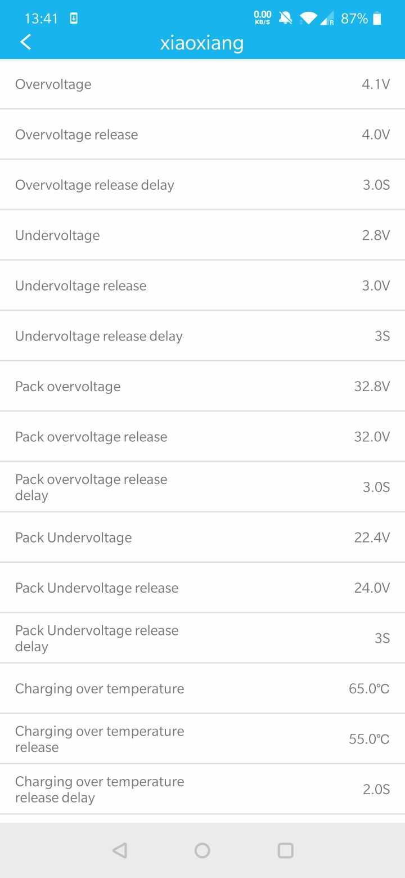
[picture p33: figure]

Figure 12: JBD Mobile app parameter settings page.
The settings on the figure above are for Li-Ion cells with an added safety margin for student use. For example, the BMS is configured to trip overvoltage protection at 4.1V, instead of the 4.2V standard for Li-Ion cells. This configuration is set on the BMS at the time of submission of the project so it may no longer be the case in the future. Always check the BMS parameter settings are set correctly for the target lithium chemistry variant before commencing test runs with loads/chargers!

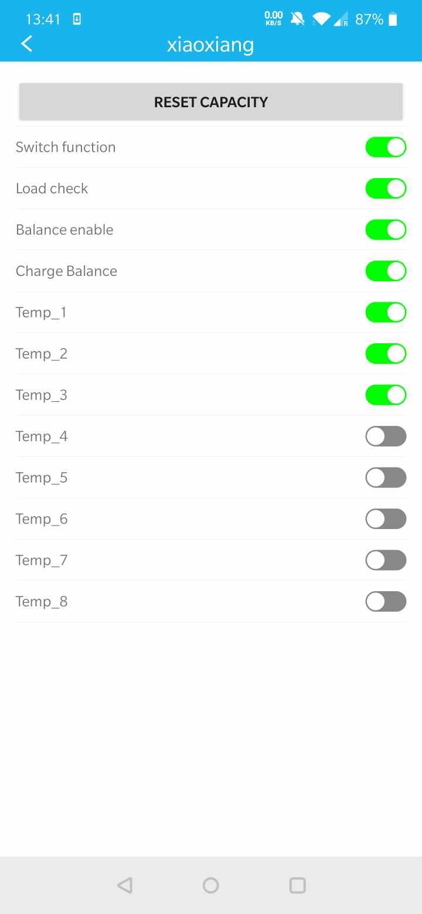
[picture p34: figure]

Figure 13: JBD Mobile app function setting page.
Finally, the figure above shows the function setting menu. Sometimes, if the battery is not connecting to the load, it’s possible the “Switch function” at the top of this menu has toggled position. Toggle it and check if the load powers on.

# Temperature sensors

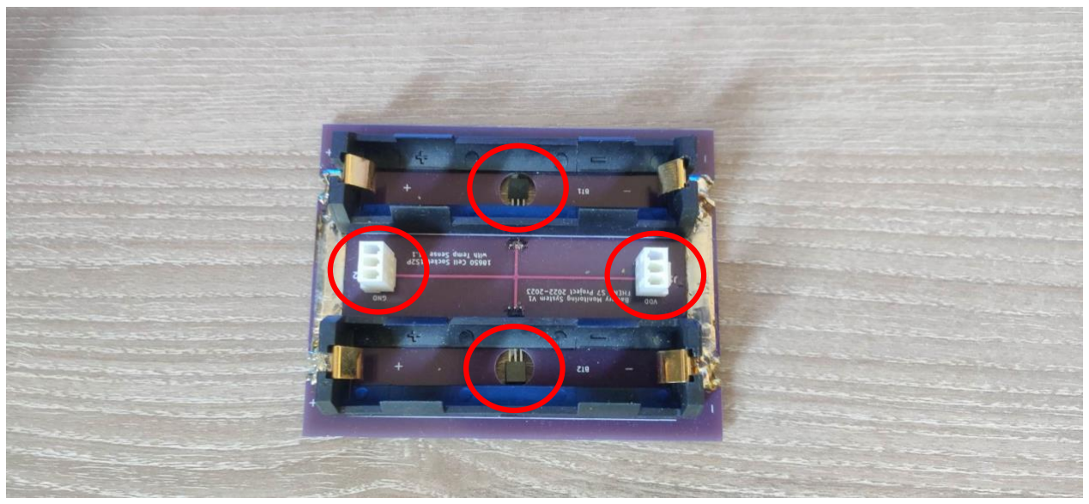
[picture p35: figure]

Figure 14: 18650 Lithium cell holder PCB with built-in DS18B20 digital temperature sensors.
The rig incorporates a number of DS18B20 digital temperature sensors, placed in the battery cell holder PCBs underneath each cell slot. The sensors are daisy chained between battery holder boards via custom 3-pin cables, carrying +5VDC, GND, and a Data wire. All sensors are wired in parallel along the path, sharing the single data line. The DS18B20 implements the OneWire communication protocol, which uses unique device IDs to interface with the sensors in the chain. That means the sensor IDs need to be read from them and hardcoded into the monitoring board Arduino code to correctly match the data from each sensor to its corresponding cell. To do this, a little Arduino program is included, courtesy of ChatGPT 4.0, for detecting all temperature sensors connected to the monitoring board and printing to the Serial monitor their unique device IDs and current temperature readings. This program will come in handy if a sensor or entire cell holder board is damaged and needs to be replaced. Simply connect the board with the special 3-pin cable (yellow/brown/black) between the battery monitoring board and one end of the cell holder board and load the program on the Arduino. Open the Serial monitor at 9600 baud rate to monitor the ID and readings print outs and hold one sensor with your fingers for a few seconds to identify it by its changing temperature reading. Write down the unique device IDs and their cell position (BT1/BT2 on the cell holder board, cell position in stack when installing in the rig) and paste them into the BatteryMonitorMCU main program in the correct places (labeled with comments). Additionally, more sensors can be attached to the rig for flexible use if needed by connecting them to the open 3-pin port on the top cell of the stack (cell 8). Again, their ID(s) will have to be retrieved and coded in the main program to work. A modification of the MATLAB application will also be required. More on that in the R&D guide.

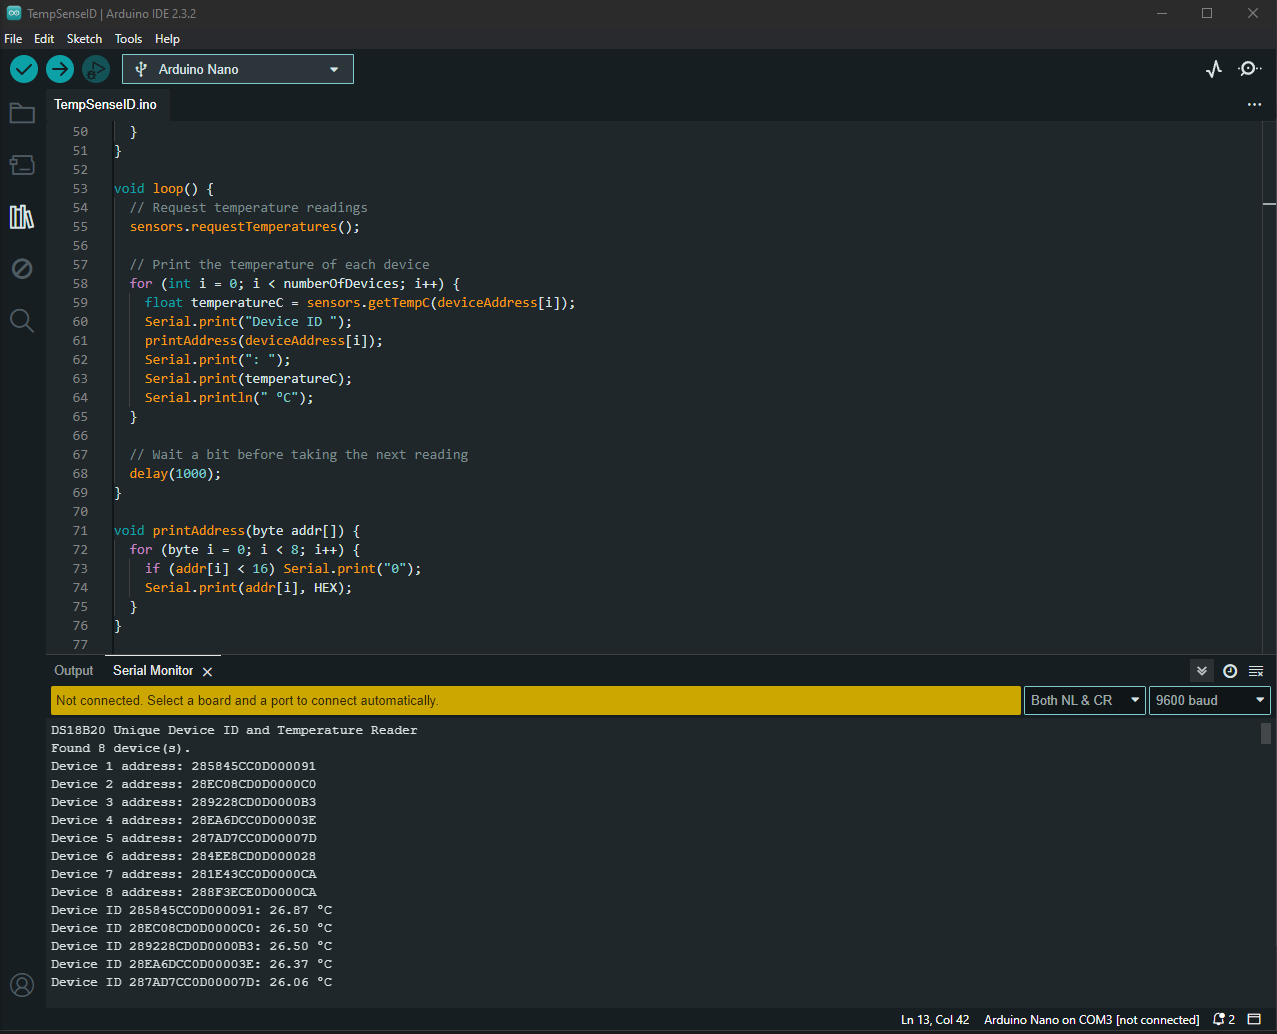
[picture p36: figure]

Figure 15: Arduino program for detecing the unique device IDs of DS18B20 temperature sensors.

# Load

To simulate the electrical load on a battery pack, a dynamic, preferably programmable load is necessary. To that end, a 150W BLDC motor typically used in electric skateboards is installed on the opposite side of the plywood board. The motor is run by a Flipsky VESC 4.12 electric speed controller (ESC) provided by Fontys. The VESC is wired with ring terminals on both its input and output side to allow easy reuse and change. Using the microUSB interface, the VESC can be configured and controlled from a PC with the VESC PC tool. The VESC tool can downloaded from the VESC website after registering a free account. There are many ways to setup the control of the motor, and this task will be done by future students assigned to this project. The end goal is to be able to create “load profiles” where the motor simulates the operating conditions of a real electric skateboard so that its electrical effects on the battery pack can be studied. More information on this can be found in the R&D document.

# Resources

All resources used in the creation of this project and/or required for its use and further development can be found in the following public GitHub repository: https://github.com/sashkoBeats/Lithium-Battery-Research-Rig

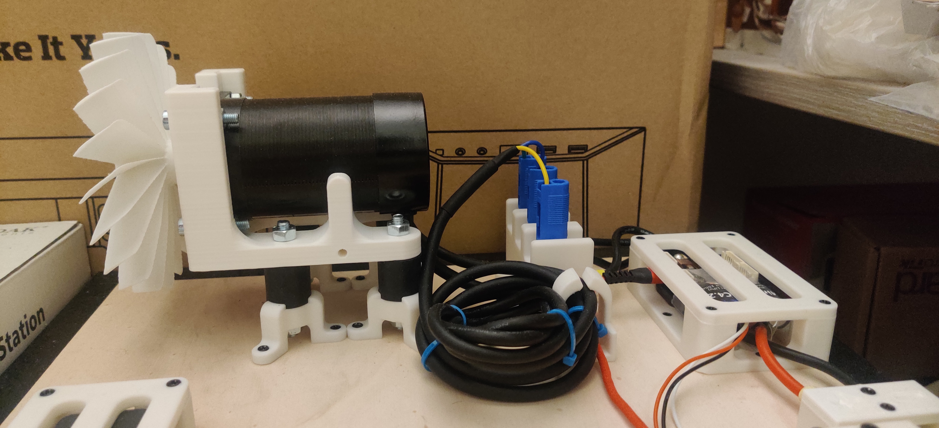
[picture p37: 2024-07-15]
Media/WIP/MotorSetup.jpg

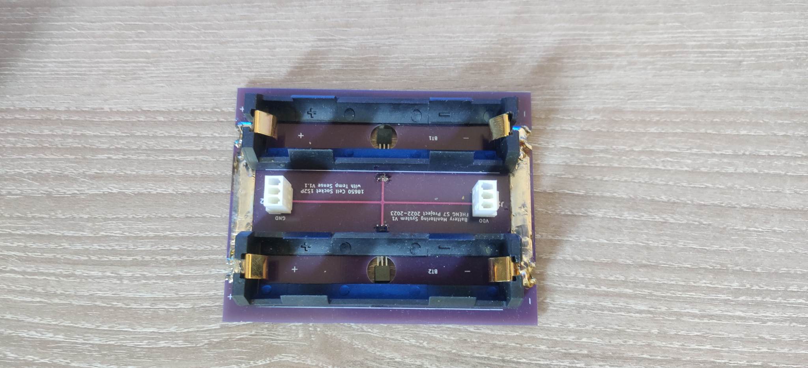
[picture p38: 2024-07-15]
Media/BatteryMountAssembled.jpg

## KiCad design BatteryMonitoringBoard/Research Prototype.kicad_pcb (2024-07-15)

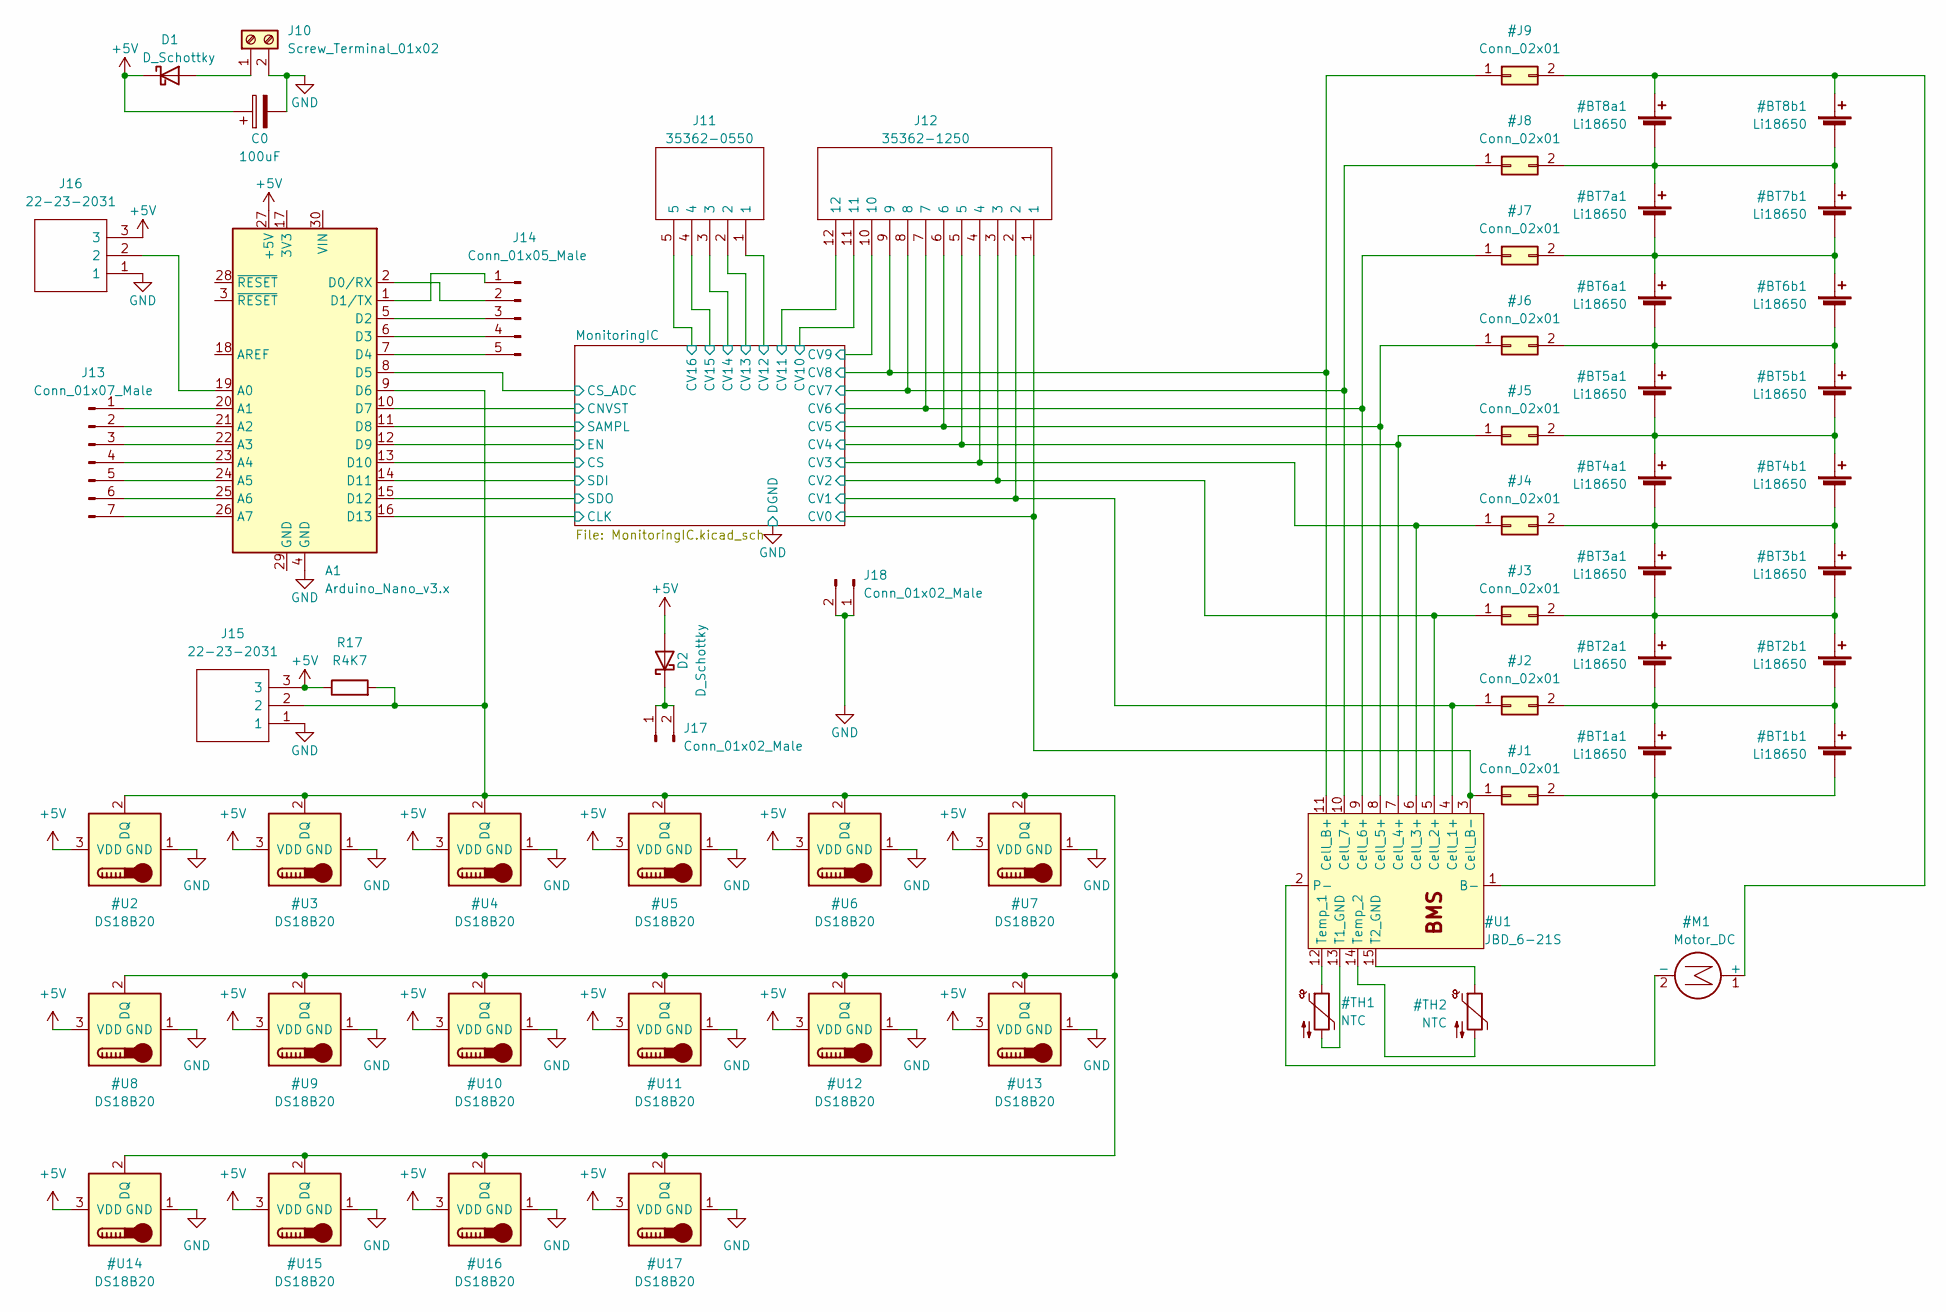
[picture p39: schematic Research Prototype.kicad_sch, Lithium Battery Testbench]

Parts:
A1: Arduino_Nano_v3.x; Arduino_Nano
C0: 100uF; CAPPRD250W50D680H1250
D1, D2: D_Schottky; SOD2512X115N
J10: Screw_Terminal_01x02; TerminalBlock_bornier-2_P5.08mm
J11: 35362-0550; SHDR5W50P0X200_1X5_1230X550X850P; Manufacturer_Part_Number 35362-0550; Mouser Part Number 538-35362-0550
J12: 35362-1250; 353621250; Manufacturer_Part_Number 35362-1250; Mouser Part Number 538-35362-1250
J13: Conn_01x07_Male; PinHeader_1x07_P2.54mm_Vertical
J14: Conn_01x05_Male
J15, J16: 22-23-2031; SHDR3W82P0X254_1X3_747X635X818P; Manufacturer_Part_Number 22-23-2031; Mouser Part Number 538-22-23-2031
J17, J18: Conn_01x02_Male; PinHeader_1x02_P2.54mm_Vertical
R17: R4K7; R_Axial_DIN0309_L9.0mm_D3.2mm_P12.70mm_Horizontal

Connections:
/MonitoringIC/CLK: A1.16 (D13); also elsewhere on the board
/MonitoringIC/CNVST: A1.10 (D7); also elsewhere on the board
/MonitoringIC/CS: A1.13 (D10); also elsewhere on the board
/MonitoringIC/CV9: J12.10; also elsewhere on the board
/MonitoringIC/CV10: J12.11; also elsewhere on the board
/MonitoringIC/CV11: J12.12; also elsewhere on the board
/MonitoringIC/CV12: J11.1; also elsewhere on the board
/MonitoringIC/CV13: J11.2; also elsewhere on the board
/MonitoringIC/CV14: J11.3; also elsewhere on the board
/MonitoringIC/CV15: J11.4; also elsewhere on the board
/MonitoringIC/CV16: J11.5; also elsewhere on the board
/MonitoringIC/EN: A1.12 (D9); also elsewhere on the board
/MonitoringIC/SAMPL: A1.11 (D8); also elsewhere on the board
/MonitoringIC/SDI: A1.14 (D11); also elsewhere on the board
/MonitoringIC/SDO: A1.15 (D12); also elsewhere on the board
unnamed: A1.1 (D1/TX), J14.1
unnamed: A1.2 (D0/RX), J14.2
unnamed: A1.5 (D2), J14.3
unnamed: A1.6 (D3), J14.4
unnamed: A1.7 (D4), J14.5
unnamed: A1.8 (D5), J14.6
unnamed: A1.19 (A0), J16.2
unnamed: A1.20 (A1), J13.1
unnamed: A1.21 (A2), J13.2
unnamed: A1.22 (A3), J13.3
unnamed: A1.23 (A4), J13.4
unnamed: A1.24 (A5), J13.5
unnamed: A1.25 (A6), J13.6
unnamed: A1.26 (A7), J13.7
unnamed: D1.2 (A), J10.1
unnamed: D2.1 (K), J17.1, J17.2

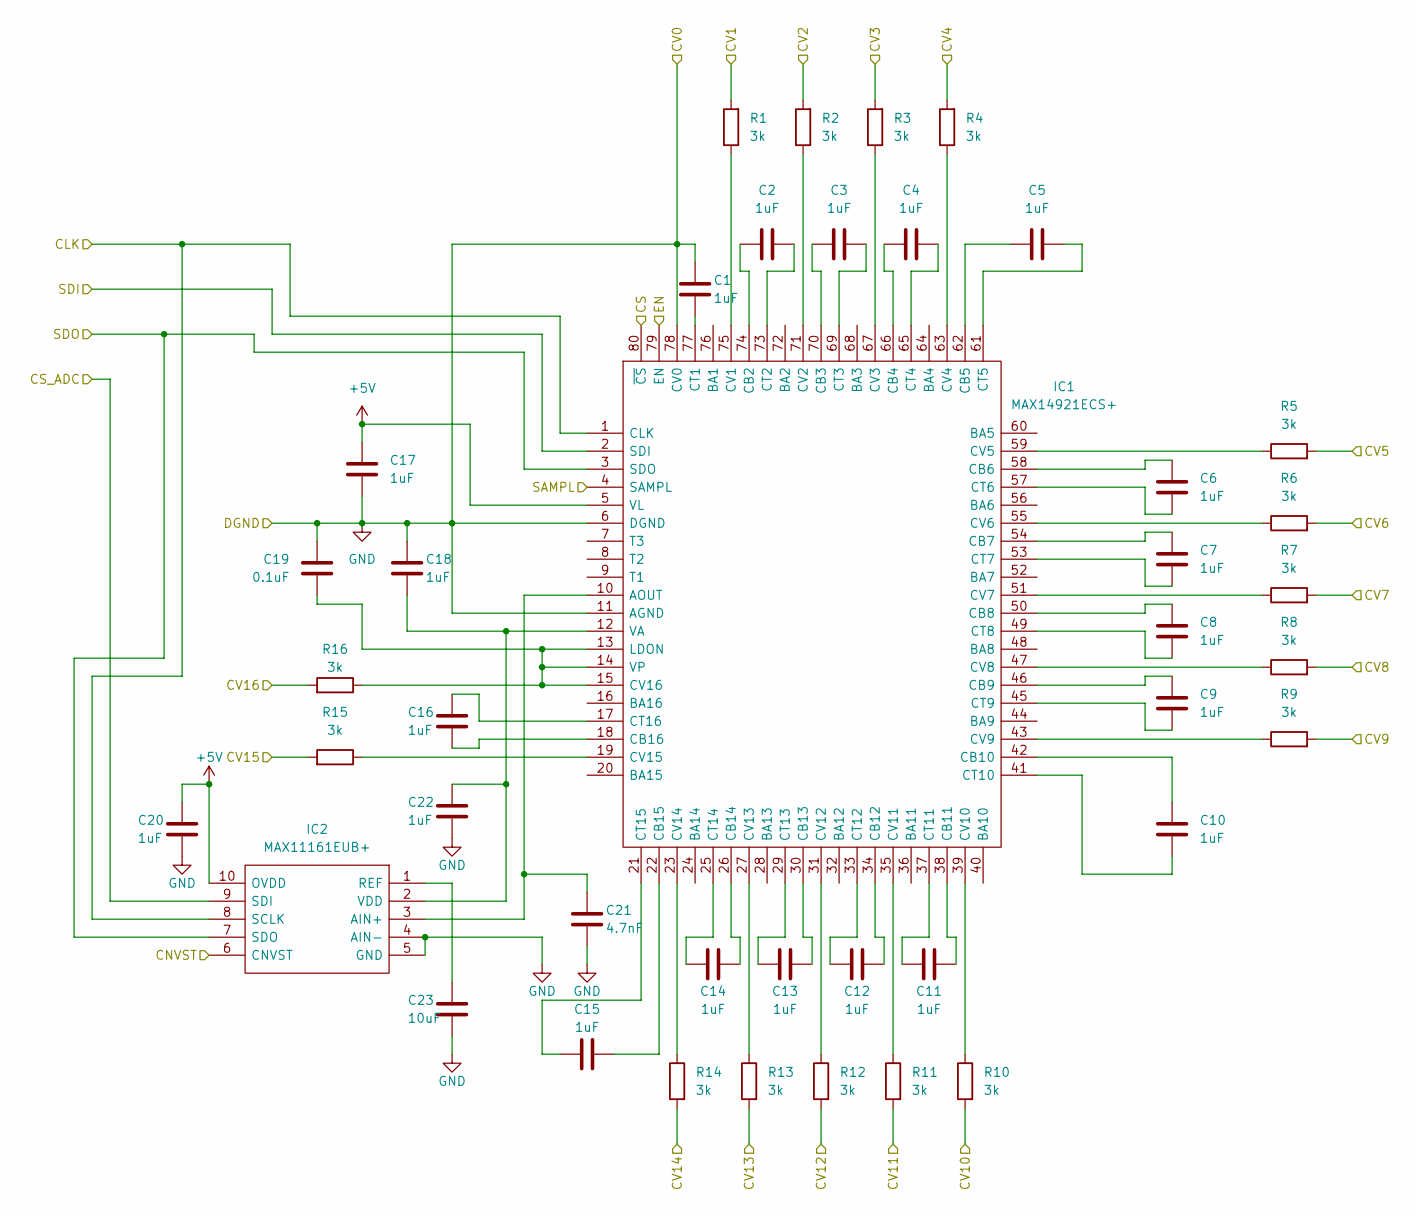
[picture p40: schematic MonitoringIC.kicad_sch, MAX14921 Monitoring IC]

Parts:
C1, C2, C3, C4, C5, C6, C7, C8, C9, C10, C11, C12, C13, C14, C15, C16, C17, C18, C20, C22: 1uF; CAPC3216X180N
C19: 0.1uF; CAPC1005X55N
C21: 4.7nF; CAPC1608X90N
C23: 10uF; CAPC2012X140N
IC1: MAX14921ECS+; QFP50P1400X1400X120-80N; Manufacturer_Part_Number MAX14921ECS+; Mouser Part Number 700-MAX14921ECS+
IC2: MAX11161EUB+; SOP50P490X110-10N; Manufacturer_Part_Number MAX11163EUB+; Mouser Part Number 700-MAX11163EUB+
R1, R2, R3, R4, R5, R6, R7, R8, R9, R10, R11, R12, R13, R14, R15, R16: 3k; ERJ3EK__0603_

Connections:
/MonitoringIC/CLK: IC1.1 (CLK), IC2.8 (SCLK); also elsewhere on the board
/MonitoringIC/CNVST: IC2.6 (CNVST); also elsewhere on the board
/MonitoringIC/CS: IC1.80 (~CS); also elsewhere on the board
/MonitoringIC/CV9: R9.2; also elsewhere on the board
/MonitoringIC/CV10: R10.2; also elsewhere on the board
/MonitoringIC/CV11: R11.2; also elsewhere on the board
/MonitoringIC/CV12: R12.2; also elsewhere on the board
/MonitoringIC/CV13: R13.2; also elsewhere on the board
/MonitoringIC/CV14: R14.2; also elsewhere on the board
/MonitoringIC/CV15: R15.2; also elsewhere on the board
/MonitoringIC/CV16: R16.2; also elsewhere on the board
/MonitoringIC/EN: IC1.79 (EN); also elsewhere on the board
/MonitoringIC/SAMPL: IC1.4 (SAMPL); also elsewhere on the board
/MonitoringIC/SDI: IC1.2 (SDI), IC2.9 (SDI); also elsewhere on the board
/MonitoringIC/SDO: IC1.3 (SDO), IC2.7 (SDO); also elsewhere on the board
unnamed: C1.2, IC1.77 (CT1)
unnamed: C2.1, IC1.73 (CT2)
unnamed: C2.2, IC1.74 (CB2)
unnamed: C3.1, IC1.69 (CT3)
unnamed: C3.2, IC1.70 (CB3)
unnamed: C4.1, IC1.65 (CT4)
unnamed: C4.2, IC1.66 (CB4)
unnamed: C5.1, IC1.61 (CT5)
unnamed: C5.2, IC1.62 (CB5)
unnamed: C6.1, IC1.58 (CB6)
unnamed: C6.2, IC1.57 (CT6)
unnamed: C7.1, IC1.54 (CB7)
unnamed: C7.2, IC1.53 (CT7)
unnamed: C8.1, IC1.50 (CB8)
unnamed: C8.2, IC1.49 (CT8)
unnamed: C9.1, IC1.46 (CB9)
unnamed: C9.2, IC1.45 (CT9)
unnamed: C10.1, IC1.42 (CB10)
unnamed: C10.2, IC1.41 (CT10)
unnamed: C11.1, IC1.37 (CT11)
unnamed: C11.2, IC1.38 (CB11)
unnamed: C12.1, IC1.34 (CB12)
unnamed: C12.2, IC1.33 (CT12)
unnamed: C13.1, IC1.30 (CB13)
unnamed: C13.2, IC1.29 (CT13)
unnamed: C14.1, IC1.26 (CB14)
unnamed: C14.2, IC1.25 (CT14)
unnamed: C15.1, IC1.21 (CT15)
unnamed: C15.2, IC1.22 (CB15)
unnamed: C16.1, IC1.17 (CT16)
unnamed: C16.2, IC1.18 (CB16)
unnamed: C18.2, C22.1, IC1.12 (VA), IC2.2 (VDD)
unnamed: C19.1, IC1.13 (LDON), IC1.14 (VP), IC1.15 (CV16), R16.1
unnamed: C21.1, IC1.10 (AOUT), IC2.3 (AIN+)
unnamed: C23.1, IC2.1 (REF)
unnamed: IC1.19 (CV15), R15.1
unnamed: IC1.23 (CV14), R14.1
unnamed: IC1.27 (CV13), R13.1
unnamed: IC1.31 (CV12), R12.1
unnamed: IC1.35 (CV11), R11.1
unnamed: IC1.39 (CV10), R10.1
unnamed: IC1.43 (CV9), R9.1
unnamed: IC1.47 (CV8), R8.1
unnamed: IC1.51 (CV7), R7.1
unnamed: IC1.55 (CV6), R6.1
unnamed: IC1.59 (CV5), R5.1
unnamed: IC1.63 (CV4), R4.1
unnamed: IC1.67 (CV3), R3.1
unnamed: IC1.71 (CV2), R2.1
unnamed: IC1.75 (CV1), R1.1

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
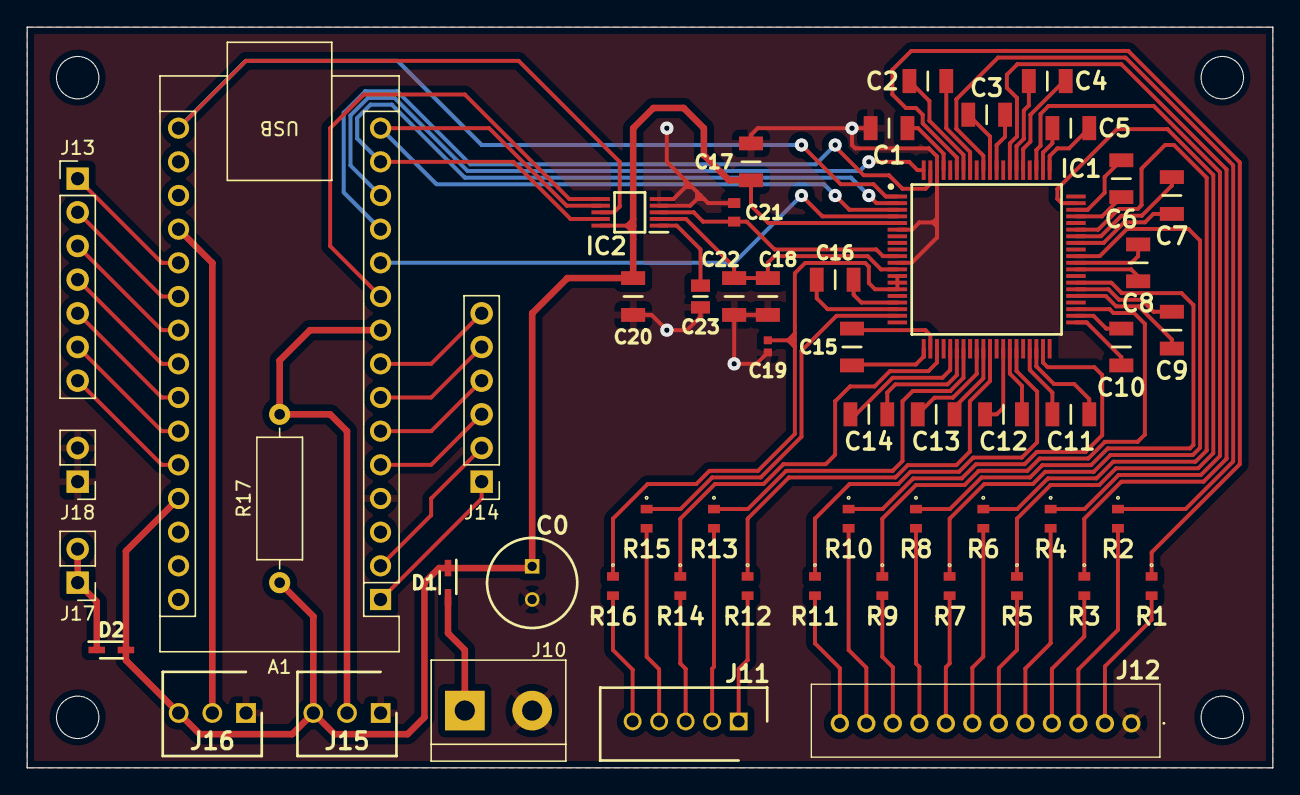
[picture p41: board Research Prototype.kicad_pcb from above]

Board: 2 copper layers, 94.0 x 55.9 mm, 55 parts (0 on the bottom side), 92 nets.

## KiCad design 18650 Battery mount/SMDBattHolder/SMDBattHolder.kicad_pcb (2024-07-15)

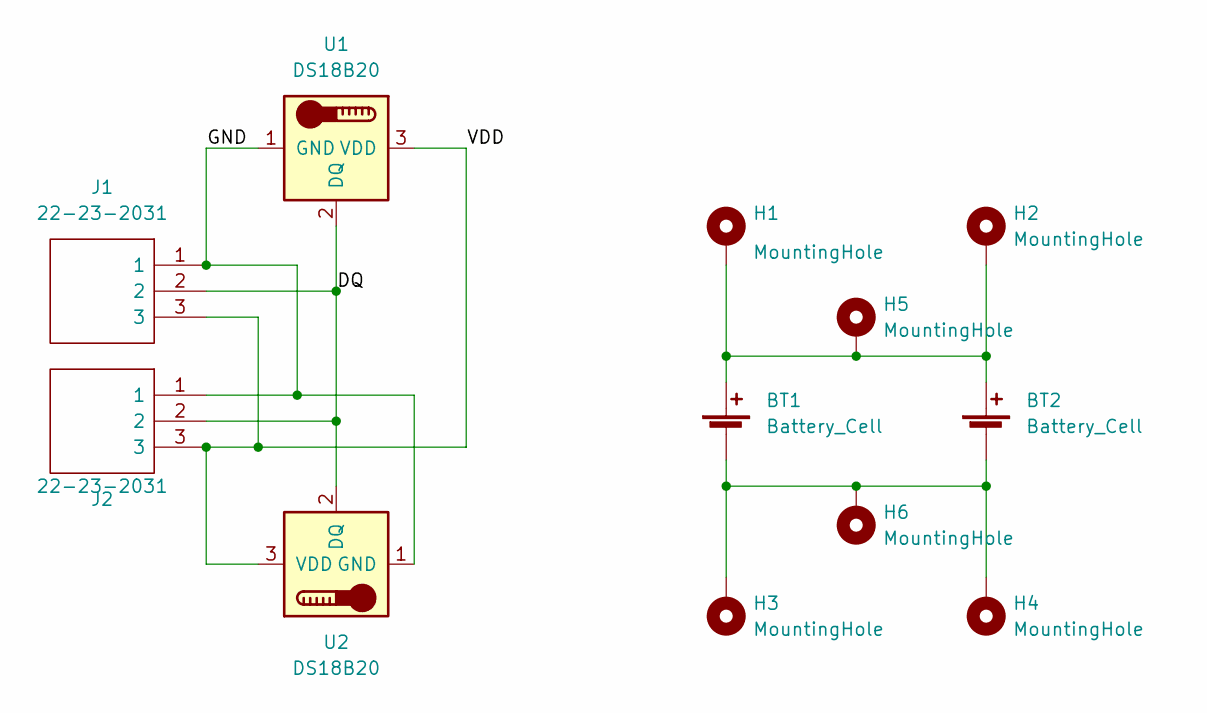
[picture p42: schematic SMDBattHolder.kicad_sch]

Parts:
BT1, BT2: Battery_Cell; ElBatterinoMounterino
H1, H2, H3, H4: MountingHole; MountingHole_3.2mm_M3_Pad_TopOnly
H5, H6: MountingHole; Long Long Pad
J1, J2: 22-23-2031; SHDR3W82P0X254_1X3_747X635X818P; Manufacturer_Part_Number 22-23-2031; Mouser Part Number 538-22-23-2031
U1, U2: DS18B20; TO-92_Inline

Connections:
/DQ: J1.2, J2.2, U1.2 (DQ), U2.2 (DQ)
/GND: J1.1, J2.1, U1.1 (GND), U2.1 (GND)
/VDD: J1.3, J2.3, U1.3 (VDD), U2.3 (VDD)
unnamed: BT1.1 (+), BT2.1 (+), H1.1, H2.1, H5.1
unnamed: BT1.2 (-), BT2.2 (-), H3.1, H4.1, H6.1

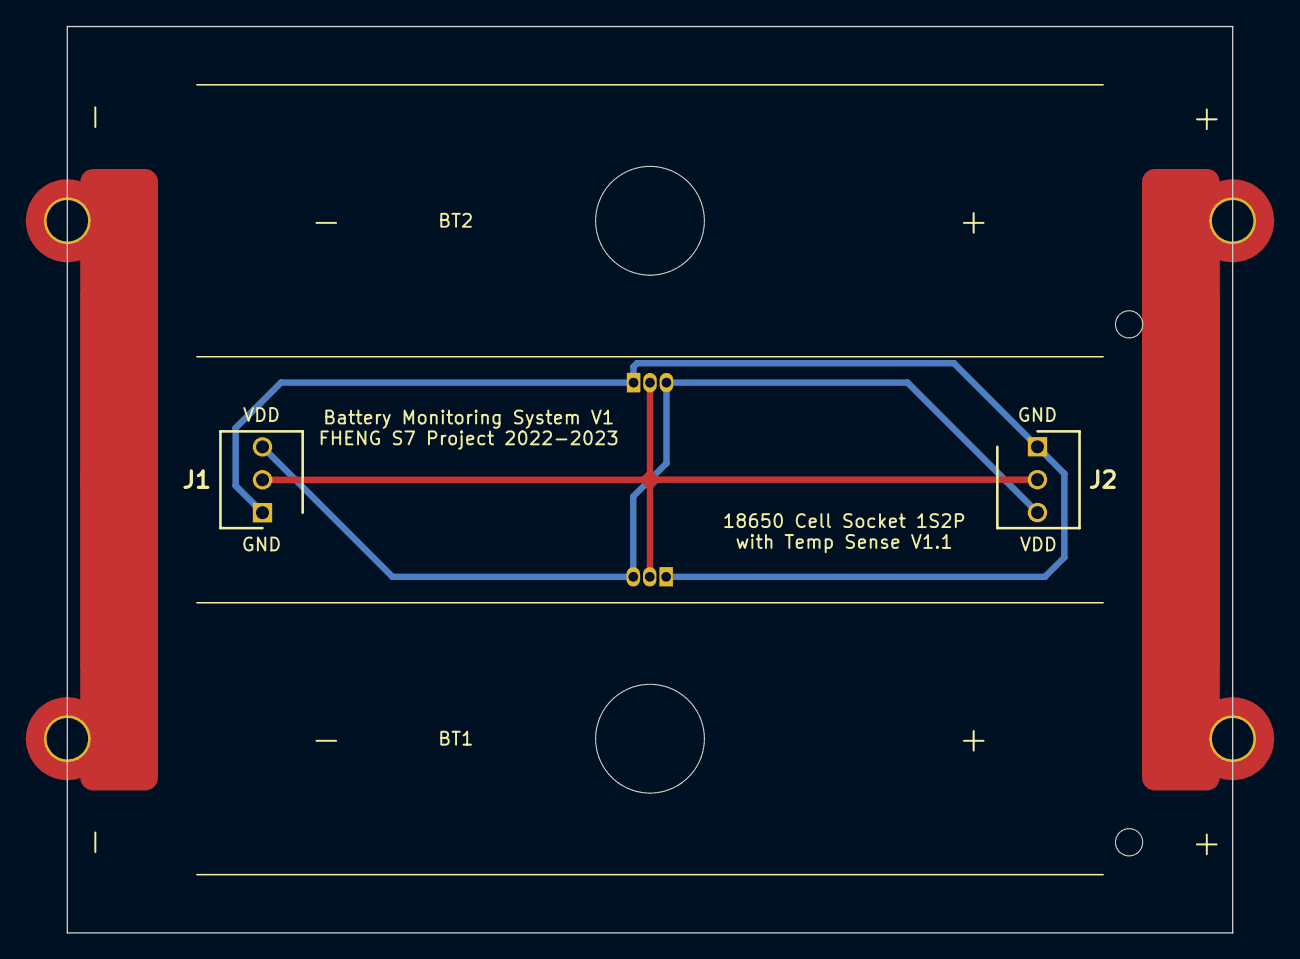
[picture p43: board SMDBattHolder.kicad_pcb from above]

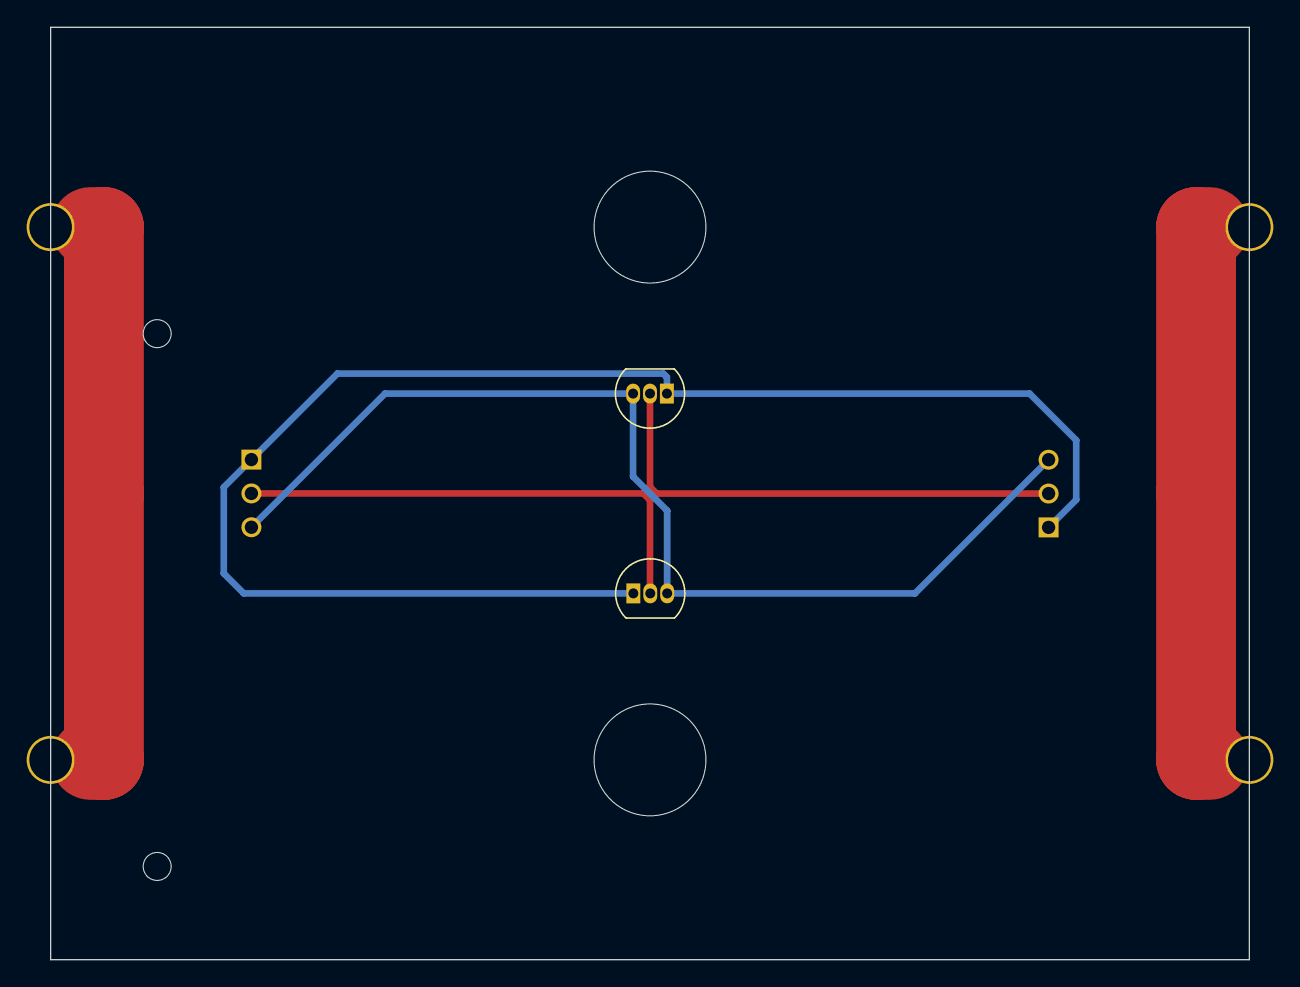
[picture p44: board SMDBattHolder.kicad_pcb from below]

Board: 2 copper layers, 90.0 x 70.0 mm, 12 parts (2 on the bottom side), 5 nets.

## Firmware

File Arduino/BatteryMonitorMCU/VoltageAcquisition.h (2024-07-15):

#ifndef VOLTAGE_ACQUISITION_INCLUDED
#define VOLTAGE_ACQUISITION_INCLUDED

#include <SPI.h>

// For Nano
#define SCLK 13 // SCLK pin
#define MISO 12 // MISO pin
#define MOSI 11 // MOSI pin

#define    MAX14921_CS 10 // MAX14921 Chip-select pin
#define    MAX14921_EN  9 // MAX14921 Enable      pin 
#define MAX14921_SAMPL  8 // MAX14921 Sample      pin
#define MAX11161_CNVST  7 // MAX11161 Conversion  pin
#define    MAX11161_CS  5 // MAX11161 Chip-select pin

#define             ECS 0x00010000
#define    SAMPLE_BIT_N 0x00200000
#define  LOW_POWER_MODE 0x00800000
#define AVERAGE_VOLTAGE 0x00180000

void SetSPISpeed(unsigned long int frequency);
void EnableSPI();
void DisableSPI();
void SetLowPowerMode(bool lowPowerModeOn);
unsigned long int TransactMAX14921(unsigned long int input);
unsigned short int TransactMAX11163();
unsigned short int SampleVoltage(unsigned char cell);
bool* GetMonitoringBits();
void Sample();
unsigned short int* SampleVoltages(unsigned char cellAmount);
bool SampleAsync();
bool SampleVoltagesAsync(unsigned short int*& result, unsigned char cellAmount);

#endif

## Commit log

2024-07-15 Initial commit 18650 Battery Mount
    [SMDBattHolder-B_Cu.gbl, SMDBattHolder-B_Mask.gbs, SMDBattHolder-B_Paste.gbp, SMDBattHolder-B_Silkscreen.gbo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]
2024-07-15 Initial commit Arduino code
    [TempSensorIDs.xlsx]
2024-07-15 Initial commit Battery Monitoring board
    [JLC-BOM.xlsx, JLC-CPL.xlsx, MonitoringIC.kicad_sch, Research Prototype Master.kicad_sch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]
2024-07-15 Initial commit Battery Monitor PC
2024-07-15 Initial commit CAD files
    [BatMt-General-standoff-V2.SLDPRT, BatMt-General-standoff-V2.STL, BatMt-General-standoff.SLDPRT, BatMt-General-standoff.STL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]
2024-07-15 Initial commit CAD files part 2
    [BLDC-Mount-Assy.SLDASM, BLDC.SLDPRT, BatMt-BLDC-Plugs.SLDPRT, BatMt-BLDC-Plugs.STL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]
2024-07-15 Initial commit CAD files part 3
    [BatMtCC-V2.SLDPRT, BatMtCC-V2.STL, BatMtCC-V3.SLDPRT, BatMtCC-V3.STL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]
